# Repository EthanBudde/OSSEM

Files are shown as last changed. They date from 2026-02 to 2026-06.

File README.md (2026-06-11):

# OSSEM
OSSEM organization repo

Espresso brewing is a thermo-fluid process where temperature, pressure, flow rate, and time directly effect extraction and flavor. Commercial smart espresso machines offer advanced control, but are expensive, closed-source, and difficult to adapt for experimental research. Existing open-source modifications improve accessibility but do not fully support research-grade measurement or instrumentation. 

This project focuses on building an open-source smart emissions monitor based on the Gaggia Classic Pro, using platforms such as Gaggiuino and Gaggia Mate for embedded control and data logging. The system will allow precise control of brewing parameters, including temperature, pressure, flow profiling, and shot timing. 

Working with the Healthy Buildings Research Lab and the Coffee Telesensing Lab at Portland State University, the machine will be adapted to support PTR-MS and UV-VIS spectroscopy for measuring volatile organic compounds (VOCs) released during espresso extraction. The result will be a flexible, open source platform that supports repeatable espresso brewing and controlled emissions research.

<p align="center">
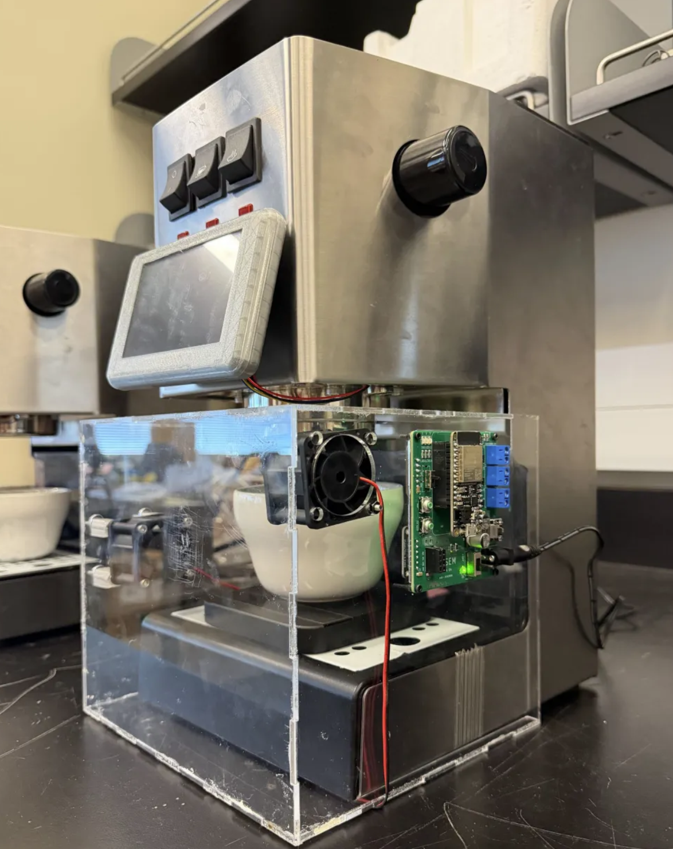
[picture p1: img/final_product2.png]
  
</p>

<p align="center">
  <em>Smart Emissions Monitor – Emissions Control Unit (ECU Final Product)</em>
</p>

<p align="center">
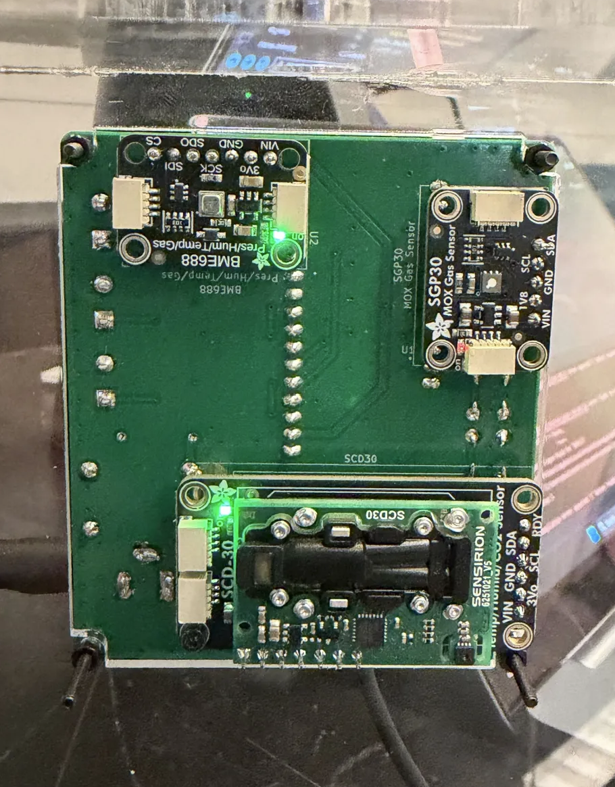
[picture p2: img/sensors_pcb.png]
  
</p>

<p align="center">
  <em>Emissions Control Unit Sensors</em>
</p>

<p align="center">
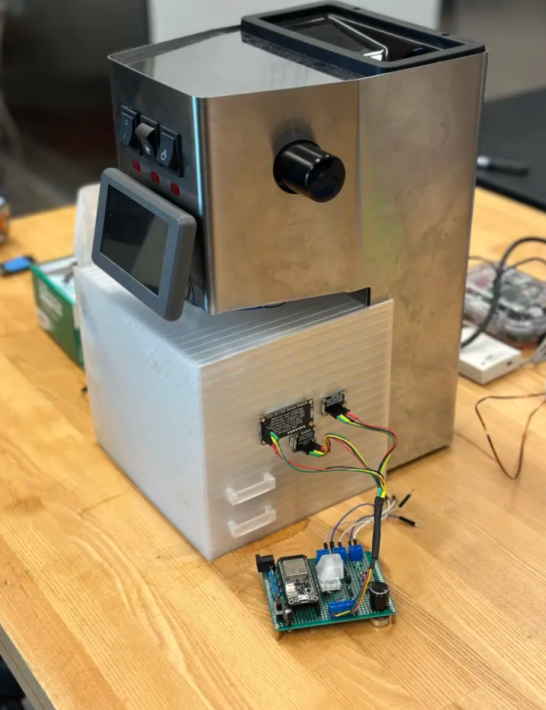
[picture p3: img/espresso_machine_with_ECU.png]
  
</p>

<p align="center">
  <em>Smart Emissions Monitor – Emissions Control Unit (ECU Prototype)</em>
</p>

<p align="center">
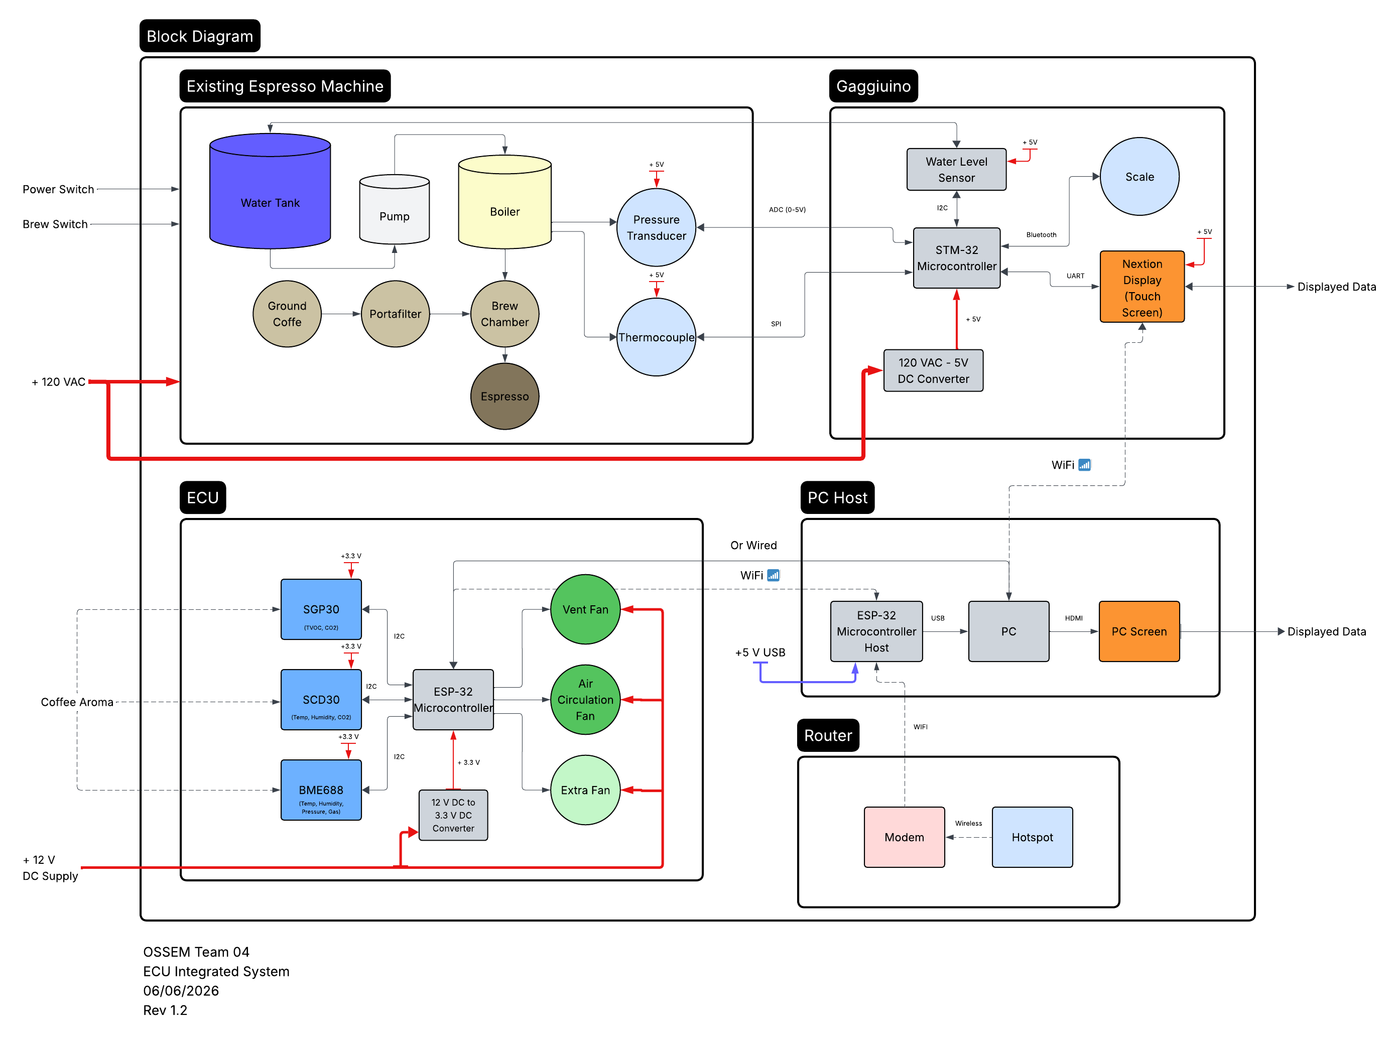
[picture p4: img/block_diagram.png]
  
</p>

<p align="center">
  <em>Smart Emissions Monitor – Block Diagram</em>
</p>

<p align="center">
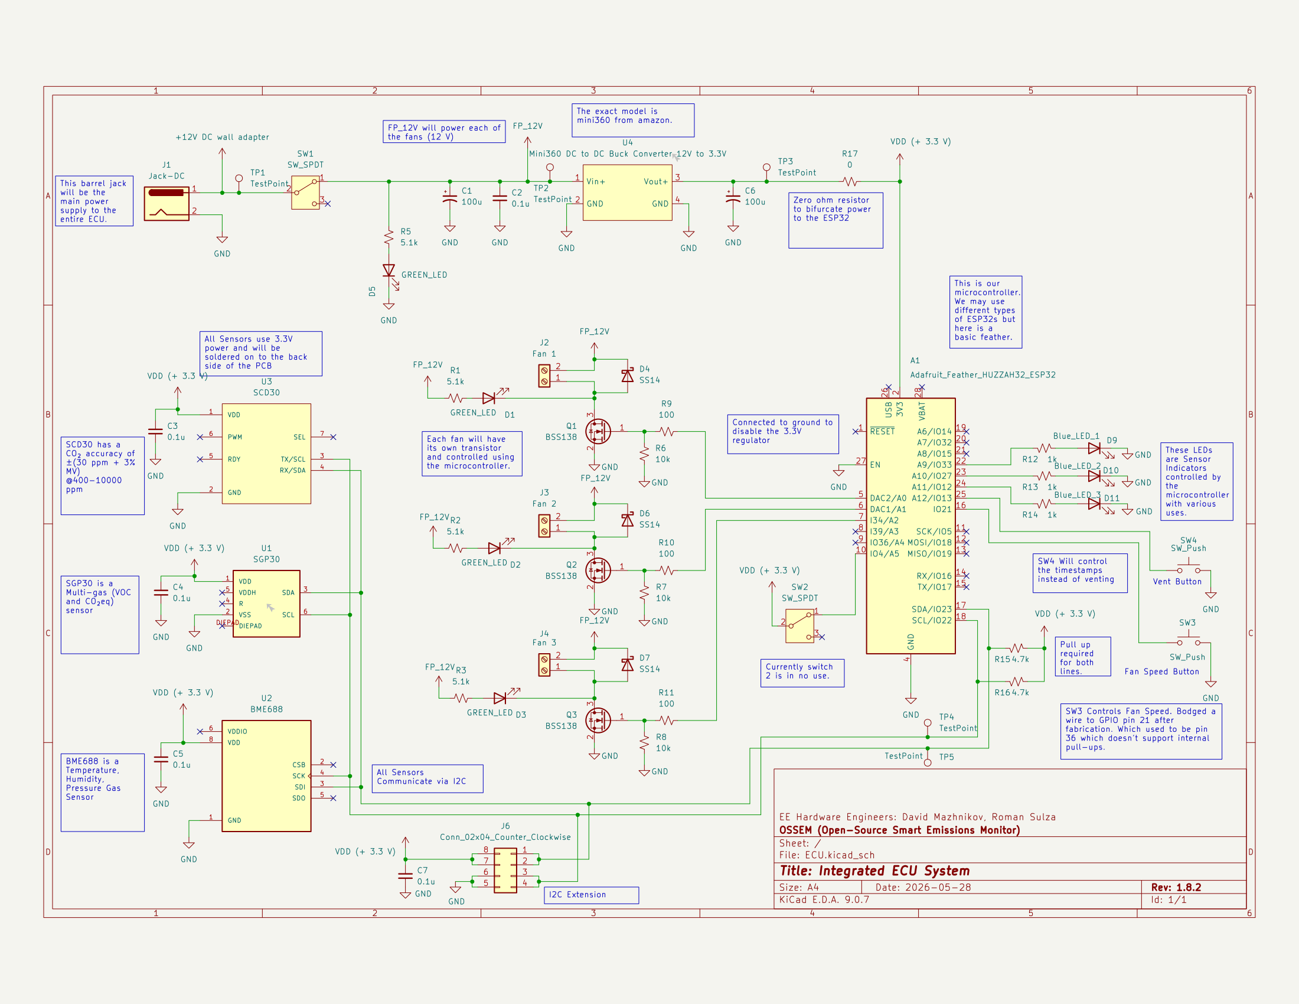
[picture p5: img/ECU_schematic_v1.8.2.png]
  
</p>

<p align="center">
  <em>Smart Emissions Monitor – Schematic v1.8.2</em>
</p>

<p align="center">
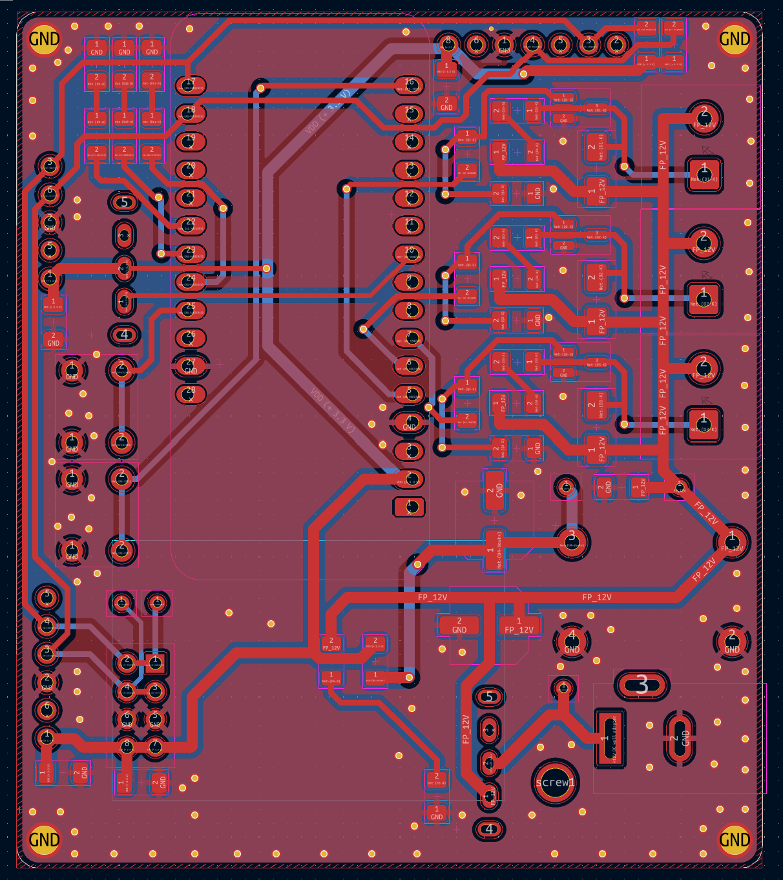
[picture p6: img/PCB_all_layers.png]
  
</p>

<p align="center">
  <em>Smart Emissions Monitor – PCB v1.8.2 </em>
</p>

<p align="center">
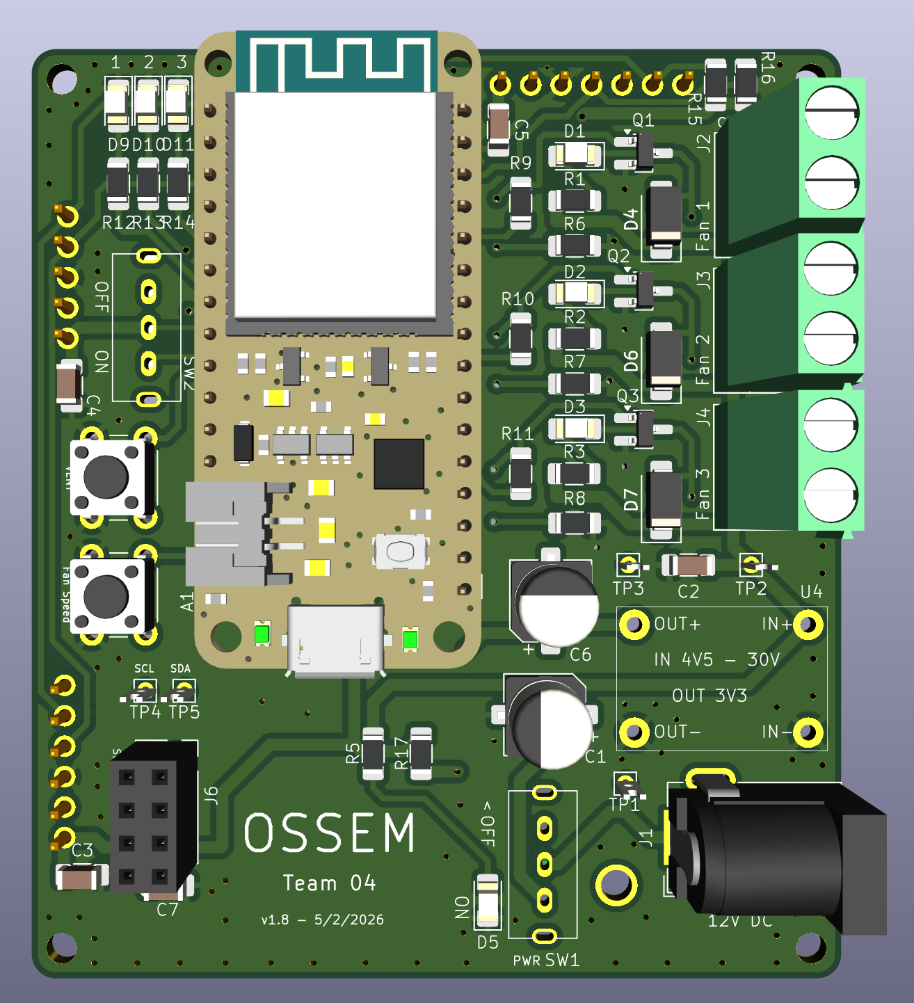
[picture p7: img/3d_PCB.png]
  
</p>

<p align="center">
  <em>Smart Emissions Monitor – 3D PCB v1.8 Front</em>
</p>

<p align="center">
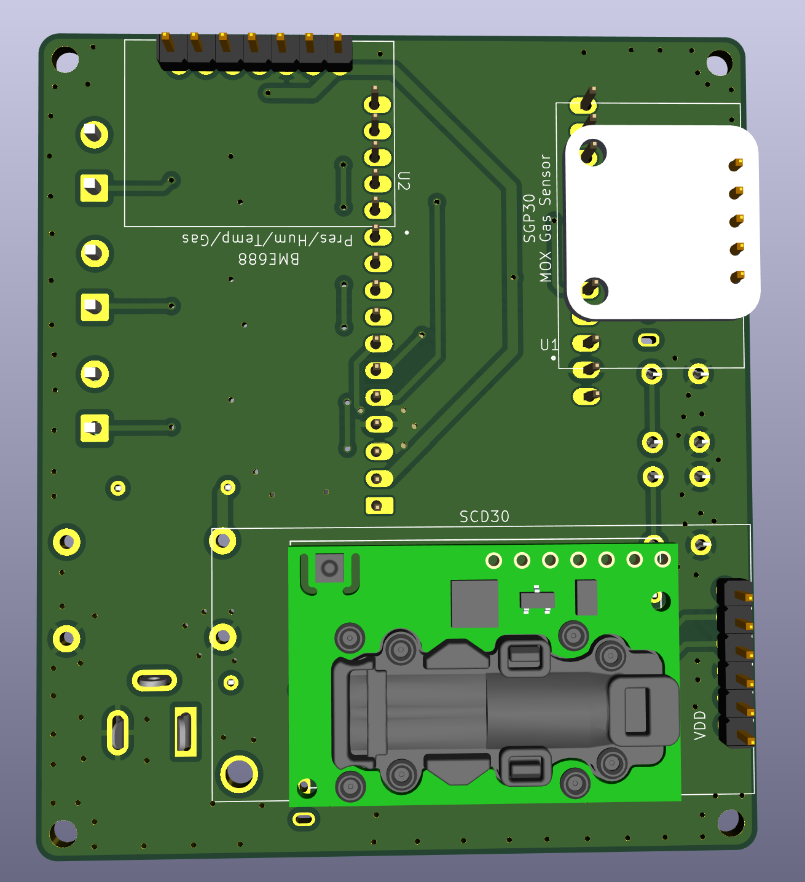
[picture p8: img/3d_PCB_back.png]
  
</p>

<p align="center">
  <em>Smart Emissions Monitor – 3D PCB v1.8 Back</em>
</p>

<p align="center">
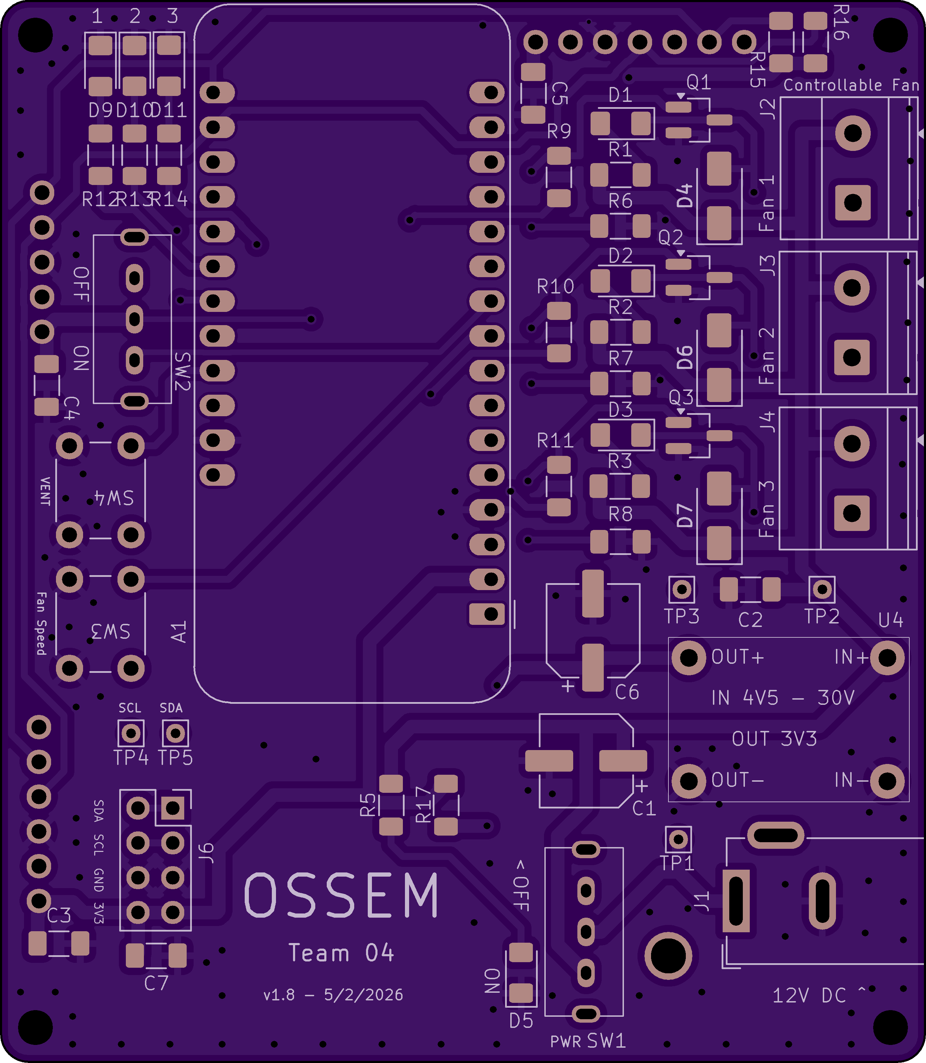
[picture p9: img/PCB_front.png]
  
</p>

<p align="center">
  <em>Smart Emissions Monitor – PCB v1.8 front</em>
</p>

<p align="center">
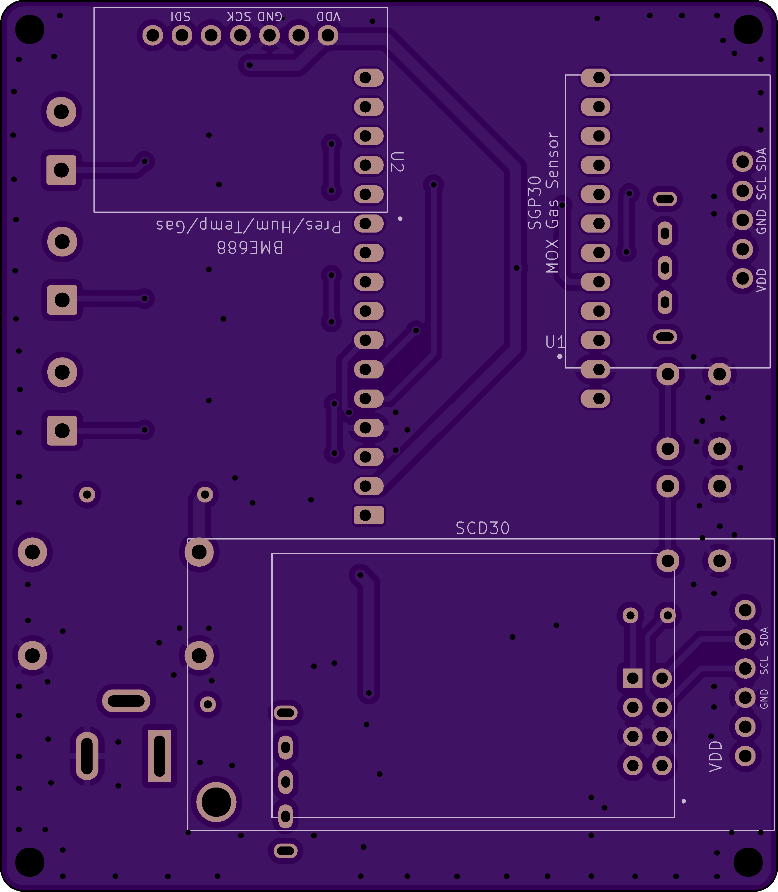
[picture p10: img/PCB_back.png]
  
</p>

<p align="center">
  <em>Smart Emissions Monitor – PCB v1.8 back</em>
</p>

<p align="center">
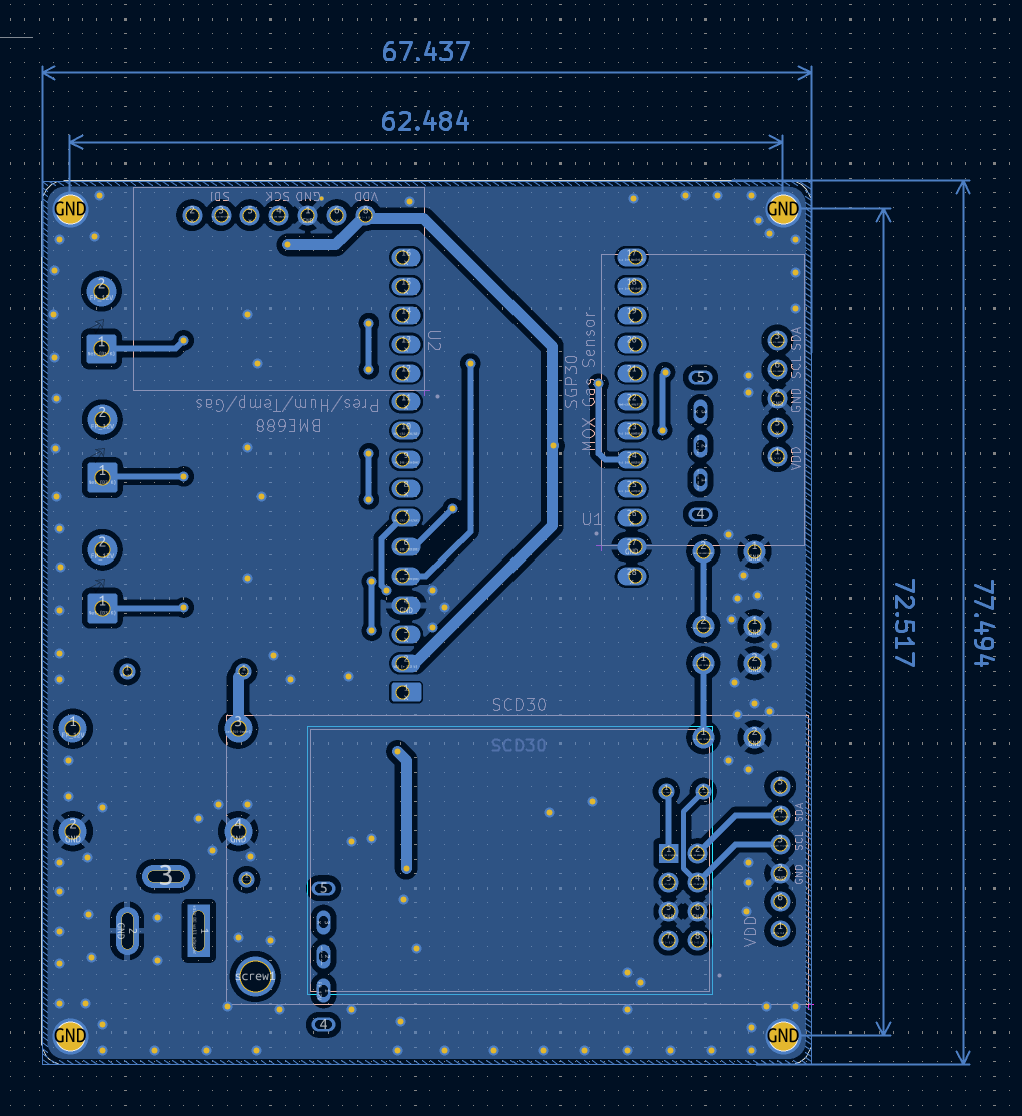
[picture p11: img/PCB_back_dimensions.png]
  
</p>

<p align="center">
  <em>Smart Emissions Monitor – PCB v1.8 back with dimensions</em>
</p>

## Acknowledgments
This project builds on:
- Gaggiuino (open-source espresso control system)
- Adafruit sensor libraries
- KiCad component libraries

PCB renders generated using OSH Park

All third-party resources are used in accordance with their respective licenses.

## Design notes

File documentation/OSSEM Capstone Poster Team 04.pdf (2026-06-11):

# Department of Electrical and Computer Engineering

# Open-source Smart Emissions Monitor

Team: Hussein Ashkanani, Ethan Budde, David Mazhnikov, Roman Sulza, Clarker Ren, Joseph Mazhnikov, John Abed, Phi Nguyen Faculty Advisors: Dr. Joshua Méndez & Dr. Elliott Gall ACKNOWLEDGEMENTS: Healthy Buildings Research Laboratory (HBRL) and Coffee and Telesensing Laboratory (COATL)

# OBJECTIVE

To develop an open-source smart emissions monitor for espresso brewing in collaboration with PSU’s Coffee and Telesensing Laboratory and Healthy Buildings Research Laboratory. The system combines a modified Gaggia Classic Pro, a custom PCB, environmental sensors, and an emissions enclosure to achieve consistent espresso brewing and repeatable emissions data collection.

# OVERVIEW

- Espresso brewing releases volatile organic compounds (VOCs) that affect indoor air quality
- Commercial smart machines are expensive, closed-source, and not designed for research
- Existing open-source modifications lack the sensing and instrumentation researchers need
- The Gaggiuino platform gives us a foundation for embedded control and data logging

# GAGGIUINO

- STM32 based functional enhancement for Gaggia Espresso Machines
- Temperature control for custom thermal, pressure, and flow profiling
- Bluetooth scale support with automatic brew stop by target weight
- Live brewing data via screen or Wi-Fi interface
- Includes local Wi-Fi connectivity for settings and monitoring

# METHODOLOGY

The team started with a Gaggiuino-modified Gaggia Classic Pro espresso machine, adding an emissions enclosure for VOC capture. An ESP32-based “Emissions Control Unit” PCB was designed for sensor reading and fan control within the enclosure.
The board integrates 3 sensors and 3 on-enclosure fans into a single PCB system. Sensor data is packetized and transmitted serially, with future design concepts utilizing network commands to a local webserver. Python tools were developed for data logging.

Figure 3: System block diagram

# TESTING & RESULTS

- Warm machine for a few minutes prior to brewing.
- Collect baseline data for 30 seconds.
- Pull a shot of espresso with the enclosure in place while simultaneously logging data using the sensor array.
- Collect post-brew data for 30 seconds.
- Remove enclosure and collect data for an additional 30 seconds.

Figure 1: Gaggia Espresso

Machine | Figure 2: Final design | COMPONENTS

Components used in the emissions monitor include sensors, a custom PCB and a ventilation system.

Figure 8: Custom PCB

Figure 9: Testing environment with PTR-MS | Figure 11: Espresso shot data, fan on slow speed
Figure 4: SCD30 sensor | Figure 5: BME688 sensor
Figure 6: SGP30 sensor | Figure 7: Mixing/External Fan

Figure 10: 3D Printed enclosure and PTR-MS

# CONCLUSION

- VOC and CO₂ emissions varied with roast age and brewing conditions.
- Methanol, Acetic Acid, Propionic Acid were among the primary compounds observed.
- Measurement speed and accuracy were limited by sensor design.
- Noisy environments create noisy data!

# FUTURE WORK

- Concurrent and post-shot regression analysis of data
- Integrating noise signals and environmental conditions
- Further system integration, including networking and onboard visualization.
- Successfully measured
temperature, humidity,
VOCs, CO₂ concentration,
and pressure throughout
brewing
- Observed correlation
between sensor data and
PTR-MS measurements
- Began parallel testing across multiple machines

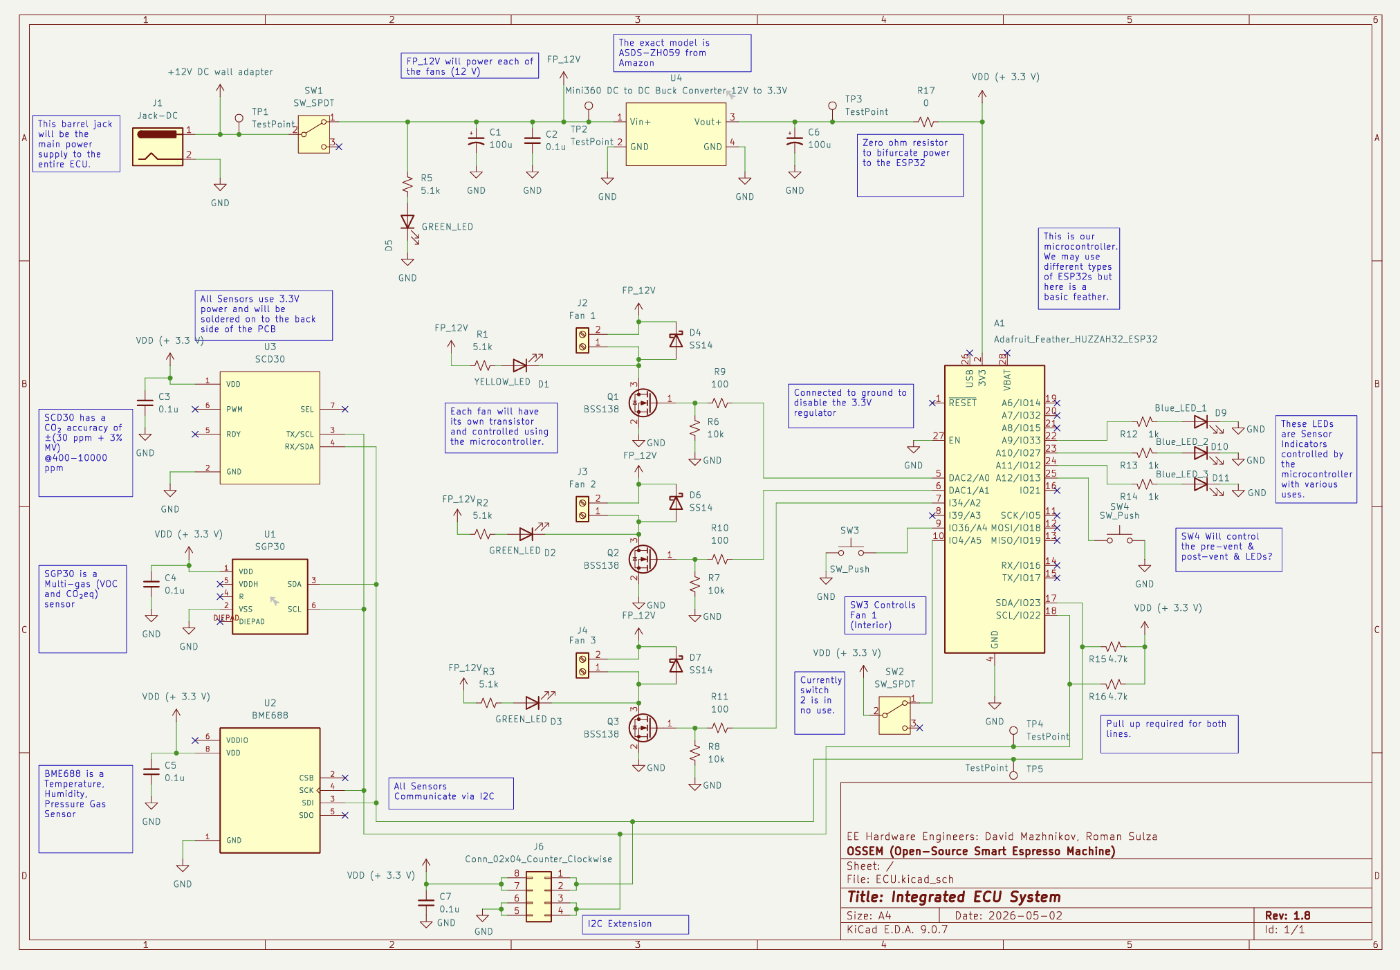
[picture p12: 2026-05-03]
img/ECU_schematic_v1.8.png

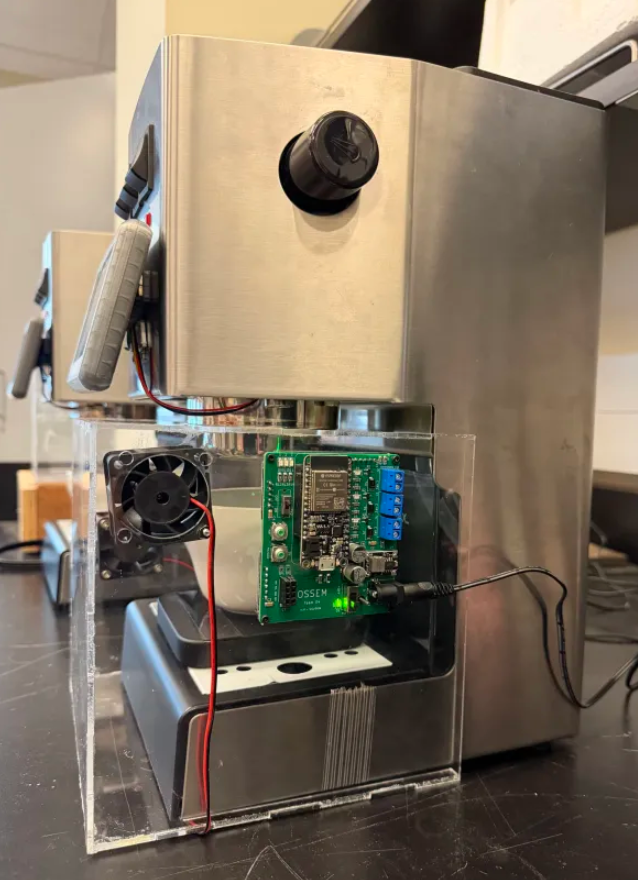
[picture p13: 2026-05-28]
img/final_product.png

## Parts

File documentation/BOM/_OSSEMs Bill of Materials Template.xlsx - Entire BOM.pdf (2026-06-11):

Bill Of Materials for: TEAM 4 - Open Source Smart Espresso Machine Last modified: 5/25/2026
BOM revision: 1.8
Qty | Mfr | Mfr Part Number Description | Dist | Dist Part Number Cost Ea. Cost Total Comments
4 Gaggia | RI9380/46 | Classic Pro E24 Espresso Machine 2024 | Amazon | B07RQ3NL76 | $457.08 $1,828.32 2 are donated? Are all these the same models? Are these bought from amazon?
2 GaggiMate | N/A | GaggiMate Pro Kit M4 K-Type + Pump Fittings | GaggiMate N/A | $212.00 | $424.00 Are these the right kits?
2 Gaggiuino | gen3-43-pro | Gaggiuino V4 PCB Kit 4.3″ Screen – GEN3 + Tank lvl + Scale | diy-efi | N/A | $325.00 | $650.00 Are these the right kits?
4 BaristaGadgets N/A | 12 Bar OPV Spring For Gaggia Classic PRO And EVO | Etsy | N/A | $12.00 | $48.00 Do we need all 4? Need to test each one if we need it or not
3 DigiKey | | ECU PCB total cost | | | $144.84 | $434.52 Price for 3 boards
1 Oshpark | | ECU PCB Fabbing costs | Oshpark | | $40.55 | $40.55 pack of 3
1 | | coffee beans | | | | $0.00
| | | | | TOTAL: | $3,425.39
VERSION INFO | | Comments

Rev
v1.8 | 5/11/2026
v1.8.1 | 5/25/2026

Links
https://www.amazon.com/Gaggia-RI9380-46-Espresso-Stainless/dp/B07RQ3NL76/ref=sr_1_1?crid=3OJE6MGPW61DH&dib=eyJ2IjoiMSJ9.eYjKLsAvj1W0J6UOi1cLWs7S2YO8OF4hQAQOlOF3g3hLJJjRMZuoTq9kSqRVxgfibjTNTAQokkwh8XOKxLYhOdfi3iOwWPR3rpvf6RqQUoixGFWXd-95crImEKKPH-aMxxHXEAhmxH4IVEVCKwkbWZhpCHDTMgAsxH_T5XagWTciojZHAUzSdV2V3VQgI8-yCoFLX5xq1GGfT73qabMzcHNR89k-2l4n2ZzoZgXIzuMGinX8iaTRX1HTunmR64dIo9db7rgI1Ui58Jy15TETksqra-XEj0mxnXHOiJN3FS8.pQ1m0DwROLVlKqMd-gxUtJx_k86bBO7aoHyDohzuF5U&dib_tag=se&keywords=Gaggia%2BClassic%2BPro%2BE24%2BEspresso%2BMachine&qid=1770954556&sprefix=gaggia%2Bclassic%2Bpro%2Be24%2Bespresso%2Bmachine%2Caps%2C223&sr=8-1&th=1 https://shop.gaggimate.eu/products/gaggimate-pro-kit
https://diy-efi.co.uk/product/gaggiuino-pro-kit-v4-gen3
https://www.etsy.com/listing/1556589768/12-bar-opv-spring-for-gaggia-classic-pro

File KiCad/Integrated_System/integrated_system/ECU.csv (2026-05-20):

Reference | Qty | Value | Description | Footprint | MANUFACTURER | MP | Datasheet
A1 | 1 | Adafruit_Feather_HUZZAH32_ESP32 | Microcontroller module with ESP32 MCU | Module:Adafruit_Feather | Adafruit |  | https://cdn-learn.adafruit.com/downloads/pdf/adafruit-huzzah32-esp32-feather.pdf
C1,C6 | 2 | 100u | Polarized capacitor, small US symbol | Capacitor_SMD:CP_Elec_6.3x7.7 | DigiKey |  | ~
C2,C3,C4,C5,C7 | 5 | 0.1u | Unpolarized capacitor, small symbol | Capacitor_SMD:C_1206_3216Metric_Pad1.33x1.80mm_HandSolder | DigiKey |  | ~
D1 | 1 | YELLOW_LED | Light emitting diode | LED_SMD:LED_1206_3216Metric_Pad1.42x1.75mm_HandSolder | DigiKey |  | ~
D2,D3,D5 | 3 | GREEN_LED | Light emitting diode | LED_SMD:LED_1206_3216Metric_Pad1.42x1.75mm_HandSolder | DigiKey |  | ~
D4,D6,D7 | 3 | SS14 | 40V 1A Schottky Diode, SMA | Diode_SMD:D_SMA | DigiKey |  | https://www.vishay.com/docs/88746/ss12.pdf
D9 | 1 | Blue_LED_1 | Light emitting diode | LED_SMD:LED_1206_3216Metric_Pad1.42x1.75mm_HandSolder | DigiKey |  | ~
D10 | 1 | Blue_LED_2 | Light emitting diode | LED_SMD:LED_1206_3216Metric_Pad1.42x1.75mm_HandSolder | DigiKey |  | ~
D11 | 1 | Blue_LED_3 | Light emitting diode | LED_SMD:LED_1206_3216Metric_Pad1.42x1.75mm_HandSolder | DigiKey |  | ~
J1 | 1 | Jack-DC | DC Barrel Jack | Connector_BarrelJack:BarrelJack_GCT_DCJ200-10-A_Horizontal | DigiKey |  | ~
J2 | 1 | Fan 1 | Generic screw terminal, single row, 01x02, script generated (kicad-library-utils/schlib/autogen/connector/) | TerminalBlock_Phoenix:TerminalBlock_Phoenix_MKDS-1,5-2-5.08_1x02_P5.08mm_Horizontal | DigiKey |  | ~
J3 | 1 | Fan 2 | Generic screw terminal, single row, 01x02, script generated (kicad-library-utils/schlib/autogen/connector/) | TerminalBlock_Phoenix:TerminalBlock_Phoenix_MKDS-1,5-2-5.08_1x02_P5.08mm_Horizontal | DigiKey |  | ~
J4 | 1 | Fan 3 | Generic screw terminal, single row, 01x02, script generated (kicad-library-utils/schlib/autogen/connector/) | TerminalBlock_Phoenix:TerminalBlock_Phoenix_MKDS-1,5-2-5.08_1x02_P5.08mm_Horizontal | DigiKey |  | ~
J6 | 1 | Conn_02x04_Counter_Clockwise | Generic connector, double row, 02x04, counter clockwise pin numbering scheme (similar to DIP package numbering), script generated (kicad-library-utils/schlib/autogen/connector/) | Connector_PinSocket_2.54mm:PinSocket_2x04_P2.54mm_Vertical | DigiKey |  | ~
Q1,Q2,Q3 | 3 | BSS138 | 50V Vds, 0.22A Id, N-Channel MOSFET, SOT-23 | Package_TO_SOT_SMD:SOT-23_Handsoldering | DigiKey |  | https://www.onsemi.com/pub/Collateral/BSS138-D.PDF
R1,R2,R3,R5 | 4 | 5.1k | Resistor, small US symbol | Resistor_SMD:R_1206_3216Metric_Pad1.30x1.75mm_HandSolder | DigiKey |  | ~
R6,R7,R8 | 3 | 10k | Resistor, small US symbol | Resistor_SMD:R_1206_3216Metric_Pad1.30x1.75mm_HandSolder | DigiKey |  | ~
R9,R10,R11 | 3 | 100 | Resistor, small US symbol | Resistor_SMD:R_1206_3216Metric_Pad1.30x1.75mm_HandSolder | DigiKey |  | ~
R12,R13,R14 | 3 | 1k | Resistor, small US symbol | Resistor_SMD:R_1206_3216Metric_Pad1.30x1.75mm_HandSolder | DigiKey |  | ~
R15,R16 | 2 | 4.7k | Resistor, small US symbol | Resistor_SMD:R_1206_3216Metric_Pad1.30x1.75mm_HandSolder | DigiKey |  | ~
R17 | 1 | 0 | Resistor, small US symbol | Resistor_SMD:R_1206_3216Metric_Pad1.30x1.75mm_HandSolder | DigiKey |  | ~
SW1,SW2 | 2 | SW_SPDT | Switch, single pole double throw | switch_DM:switch_dm | DigiKey |  | ~
SW3,SW4 | 2 | SW_Push | Push button switch, generic, two pins | Button_Switch_THT:SW_PUSH_6mm | DigiKey |  | ~
TP1,TP2,TP3,TP4,TP5 | 5 | TestPoint | test point | Connector_Pin:Pin_D0.7mm_L6.5mm_W1.8mm_FlatFork | DigiKey |  | ~
U3 | 1 | SCD30 |  | SCD30:MODULE_SCD30 | Sensirion
U4 | 1 | Mini360 DC to DC Buck Converter 12V to 3.3V |  | Library:Mini360 | Amazon
U2 | 1 | BME688 |  | BME680:PSON80P300X300X100-8N | Bosch Sensortec | BME680
U1 | 1 | SGP30 |  | SGP30:SGP30 | Adafruit | SGP30

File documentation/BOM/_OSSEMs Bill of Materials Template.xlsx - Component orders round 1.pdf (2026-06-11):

Bill Of Materials for: TEAM 4 - Open Source Smart Espresso Machine Last modified: 2/23/2026
BOM revision: 1.0r1
Qty | Mfr | Mfr Part Number | Description | Dist | Dist Part Number Cost Ea. | Cost Total | Comments | Links
4 Sensirion | SHT40 | Temp/Humidity sensor | Adafruit | 4885 | $5.95 | $23.80 | https://www.adafruit.com/product/4885?srsltid=AfmBOor-G3Y08UFehkjBrZJl_1ohO81TSDiFq6n9P5MXHyIh9_Jythr6
2 Sensirion | SGP30 | TVOC sensor | Adafruit | 3709 | $17.50 | $35.00
4 Sensirion | STC31-C-R3 | CO2 sensor | Mouser | 403-STC31-C-R3 | $31.28 | $125.12 | https://www.mouser.com/ProductDetail/Sensirion/STC31-C-R3?qs=wT7LY0lnAe37rCJTiHe%252BrQ%3D%3D&utm_id=9491304176&utm_source=google&utm_medium=cpc&utm_marketing_tactic=amercorp&gad_source=1&gad_campaignid=9491304176&gclid=CjwKCAiAkvDMBhBMEiwAnUA9BS0FUsJTmBF2uRvVsmqSKQCmll1pmuDwEYrxInVqTBzZ3w86c7Lz1RoCEFAQAvD_BwE
4 Adafruit | N/A | microSD card reader | Adafruit | 4682 | $3.50 | $14.00 | https://www.adafruit.com/product/4682#technical-details
4 Sandisk | SDSQXVF-032G-AN6MA microSD card, 32Gb | Sandisk | N/A | $10.49 | $41.96 generic, can be bought elsewhere https://www.sandisk.com/products/memory-cards/microsd-cards/sandisk-extreme-uhs-i-microsd-160-mbps?sku=SDSQXVF-032G-AN6MA
1 DBit | N300 | WiFi router | Amazon | N/A | $19.99 | $19.99 doesn't have to be this one | https://www.amazon.com/Setup-Wireless-Wi-Fi-Router-Internet/dp/B0CGLWPS5T?adgrpid=187821077233&dib=eyJ2IjoiMSJ9.Nok0yJVI5JQrHH3ioK6vwmW0p57kY3Ahcop6uhNaZ7WOI6yofJoF2ATOQLQjTjsSOijmAmuodI0VpVtHC_SbwuGt3u20JfSQzoflAOFXbyQxn6sf8AYssmg0YxAGGTweHEl_8lm6CAI2iayAbyJWdquZMO4tz14IFnjo8IlqH3MekMqna1u2GpkjJmcpFc9WNxv2L209gv8nyhZsmCUq-QifDoHT8OeXtRDy6qKME3s.auvnQRRe4h6CUfRDSmM4-avIqgUTDcTb4Njg7G5U5V0&dib_tag=se&hvadid=779676863753&hvdev=c&hvexpln=0&hvlocphy=9032925&hvnetw=g&hvocijid=8159785600867422257--&hvqmt=e&hvrand=8159785600867422257&hvtargid=kwd-347025567326&hydadcr=24140_13858981_2335143&keywords=inexpensive+wifi+router&mcid=f0f822e3139338c0bbd46435e94e2274&qid=1771874551&sr=8-4
| | | | | TOTAL: | $259.87

https://www.adafruit.com/product/4885?srsltid=AfmBOor-G3Y08UFehkjBrZJl_1ohO81TSDiFq6n9P5MXHyIh9_Jythr6

https://www.mouser.com/ProductDetail/Sensirion/STC31-C-R3?qs=wT7LY0lnAe37rCJTiHe%252BrQ%3D%3D&utm_id=9491304176&utm_source=google&utm_medium=cpc&utm_marketing_tactic=amercorp&gad_source=1&gad_campaignid=9491304176&gclid=CjwKCAiAkvDMBhBMEiwAnUA9BS0FUsJTmBF2uRvVsmqSKQCmll1pmuDwEYrxInVqTBzZ3w86c7Lz1RoCEFAQAvD_BwE

https://www.sandisk.com/products/memory-cards/microsd-cards/sandisk-extreme-uhs-i-microsd-160-mbps?sku=SDSQXVF-032G-AN6MAhttps://www.amazon.com/Setup-Wireless-Wi-Fi-Router-Internet/dp/B0CGLWPS5T?adgrpid=187821077233&dib=eyJ2IjoiMSJ9.Nok0yJVI5JQrHH3ioK6vwmW0p57kY3Ahcop6uhNaZ7WOI6yofJoF2ATOQLQjTjsSOijmAmuodI0VpVtHC_SbwuGt3u20JfSQzoflAOFXbyQxn6sf8AYssmg0YxAGGTweHEl_8lm6CAI2iayAbyJWdquZMO4tz14IFnjo8IlqH3MekMqna1u2GpkjJmcpFc9WNxv2L209gv8nyhZsmCUq-QifDoHT8OeXtRDy6qKME3s.auvnQRRe4h6CUfRDSmM4-avIqgUTDcTb4Njg7G5U5V0&dib_tag=se&hvadid=779676863753&hvdev=c&hvexpln=0&hvlocphy=9032925&hvnetw=g&hvocijid=8159785600867422257--&hvqmt=e&hvrand=8159785600867422257&hvtargid=kwd-347025567326&hydadcr=24140_13858981_2335143&keywords=inexpensive+wifi+router&mcid=f0f822e3139338c0bbd46435e94e2274&qid=1771874551&sr=8-4

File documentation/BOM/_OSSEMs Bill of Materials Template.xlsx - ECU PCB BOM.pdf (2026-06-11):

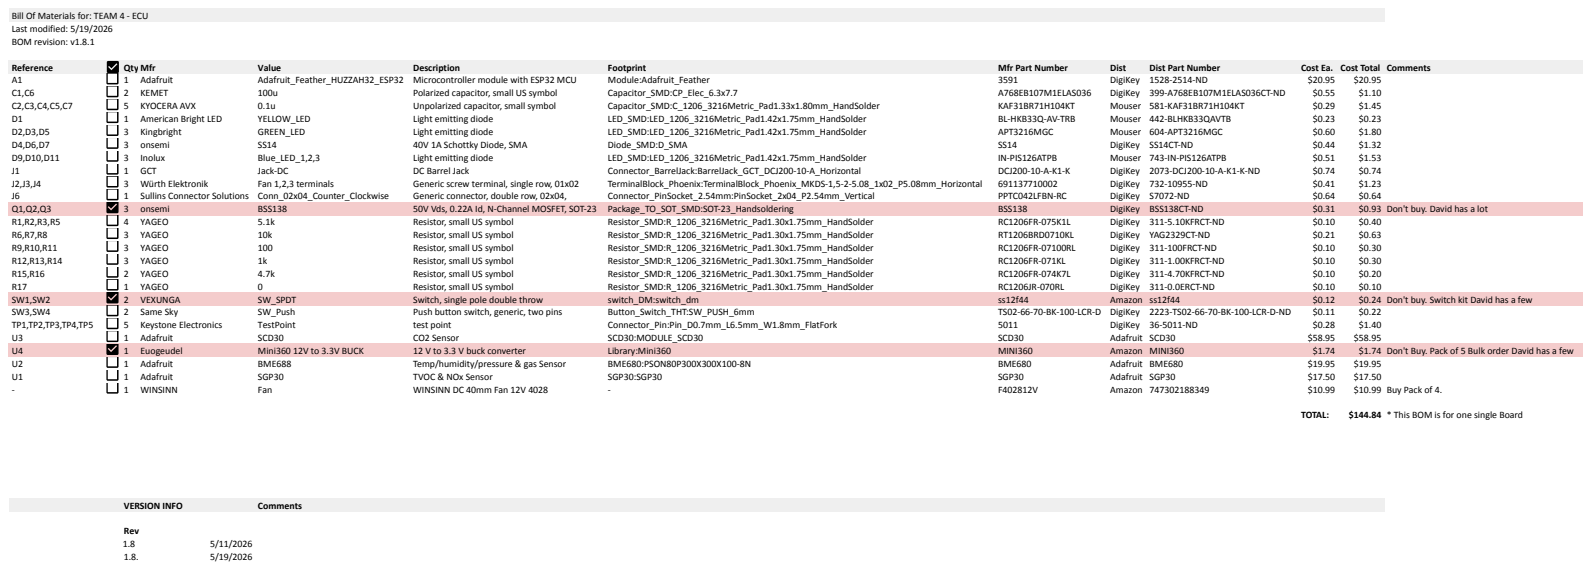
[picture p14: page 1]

Bill Of Materials for: TEAM 4 - ECU
Last modified: 5/19/2026 BOM revision: v1.8.1

Links https://www.digikey.com/en/products/detail/adafruit-industries-llc/3591/8119805?gclsrc=aw.ds&gad_source=1&gad_campaignid=20243136172&gbraid=0AAAAADrbLlhzLx615ba9QK59Pt4o19z2d&gclid=CjwKCAjwzevPBhBaEiwAplAxvjMS0UebVL3pfVtJB-cmnz0C0aDQNIIBjvmk42GUCftOvSaBqtOfDRoC3F0QAvD_BwE | https://cdn-learn.adafruit.com/downloads/pdf/adafruit-huzzah32-esp32-feather.pdf https://www.digikey.com/en/products/detail/kemet/A768EB107M1ELAS036/13420071?_gl=1*1azxihs*_up*MQ..*_gs*MQ.. https://www.mouser.com/ProductDetail/KYOCERA-AVX/KAF31BR71H104KT?qs=Jm2GQyTW%2Fbiqw6WjbGTB4g%3D%3D

https://www.mouser.com/ProductDetail/American-Bright-LED/BL-HKB33Q-AV-TRB?qs=Y0Uzf4wQF3l5aAeA8gsNCw%3D%3Dhttps://www.mouser.com/ProductDetail/Kingbright/APT3216MGC?qs=85uWm5%252BqJhXwVT90wiXd0g%3D%3D
https://www.digikey.com/en/products/detail/onsemi/SS14/965474 | https://www.vishay.com/docs/88746/ss12.pdf https://www.mouser.com/ProductDetail/Inolux/IN-PIS126ATPB?qs=G4MbTVxgV4GdC%252B%2F7gWg4nw%3D%3D
https://www.digikey.com/en/products/detail/gct/DCJ200-10-A-K1-K/9859579 https://www.digikey.com/en/products/detail/w%C3%BCrth-elektronik/691137710002/6644051 https://www.digikey.com/en/products/detail/sullins-connector-solutions/PPTC042LFBN-RC/810211 https://www.digikey.com/en/products/detail/onsemi/BSS138/244210 | https://www.onsemi.com/pub/Collateral/BSS138-D.PDF https://www.digikey.com/en/products/detail/yageo/RC1206FR-075K1L/728947 https://www.digikey.com/en/products/detail/yageo/RT1206BRD0710KL/1079472 https://www.digikey.com/en/products/detail/yageo/RC1206FR-07100RL/728491 https://www.digikey.com/en/products/detail/yageo/RC1206FR-071KL/728387 https://www.digikey.com/en/products/detail/yageo/RC1206FR-074K7L/728887 https://www.digikey.com/en/products/detail/yageo/RC1206JR-070RL/729184 https://www.amazon.com/dp/B0FG2TSLFC?ref=ppx_yo2ov_dt_b_fed_asin_title https://www.digikey.com/en/products/detail/same-sky-formerly-cui-devices-/TS02-66-70-BK-100-LCR-D/15634375?gclsrc=aw.ds&gad_source=1&gad_campaignid=20243136172&gbraid=0AAAAADrbLlhzLx615ba9QK59Pt4o19z2d&gclid=CjwKCAjwzevPBhBaEiwAplAxvv05tiw5cxMKHEIVxApXS9Wkp_bn8_xQFE9yDjJJWQSEgau41IJNmBoCpNAQAvD_BwE https://www.digikey.com/en/products/detail/keystone-electronics/5011/255333?gclsrc=aw.ds&gad_source=1&gad_campaignid=20228387720&gbraid=0AAAAADrbLlg9c50h6VvdakiVyJlQI8ZUM&gclid=CjwKCAjwzevPBhBaEiwAplAxvneNRsBU5R2wlxwfkJ7Gw7UYle7eGH3WnVuUGJn3NhPefgVtUH8TshoCnboQAvD_BwE https://www.adafruit.com/product/4867?srsltid=AfmBOopUPcTik5R2PO1EXHg9ZWgs2Y4jIcgymbVyIzx_xBf9B6JA89ov https://www.amazon.com/dp/B0BVFYXPQ8?ref=ppx_yo2ov_dt_b_fed_asin_title&th=1 https://www.adafruit.com/product/5046?gad_source=1&gad_campaignid=642608547&gbraid=0AAAAADx9JvSyw7y6eC_0nI95rRCuwBXqs&gclid=CjwKCAjwzevPBhBaEiwAplAxvum0O3m37Qx6Yu7pL77do2Y3pFkyOlGOD-MY3JrO3A6TvI0_rkeDdBoCuVoQAvD_BwE https://www.adafruit.com/product/3709?srsltid=AfmBOorbfc38_rf33Igl14sY4RIQvwuWvfZmwvBepgxOHmZKZLNTboNX https://www.amazon.com/dp/B0D3FXFG93?ref=ppx_yo2ov_dt_b_fed_asin_title

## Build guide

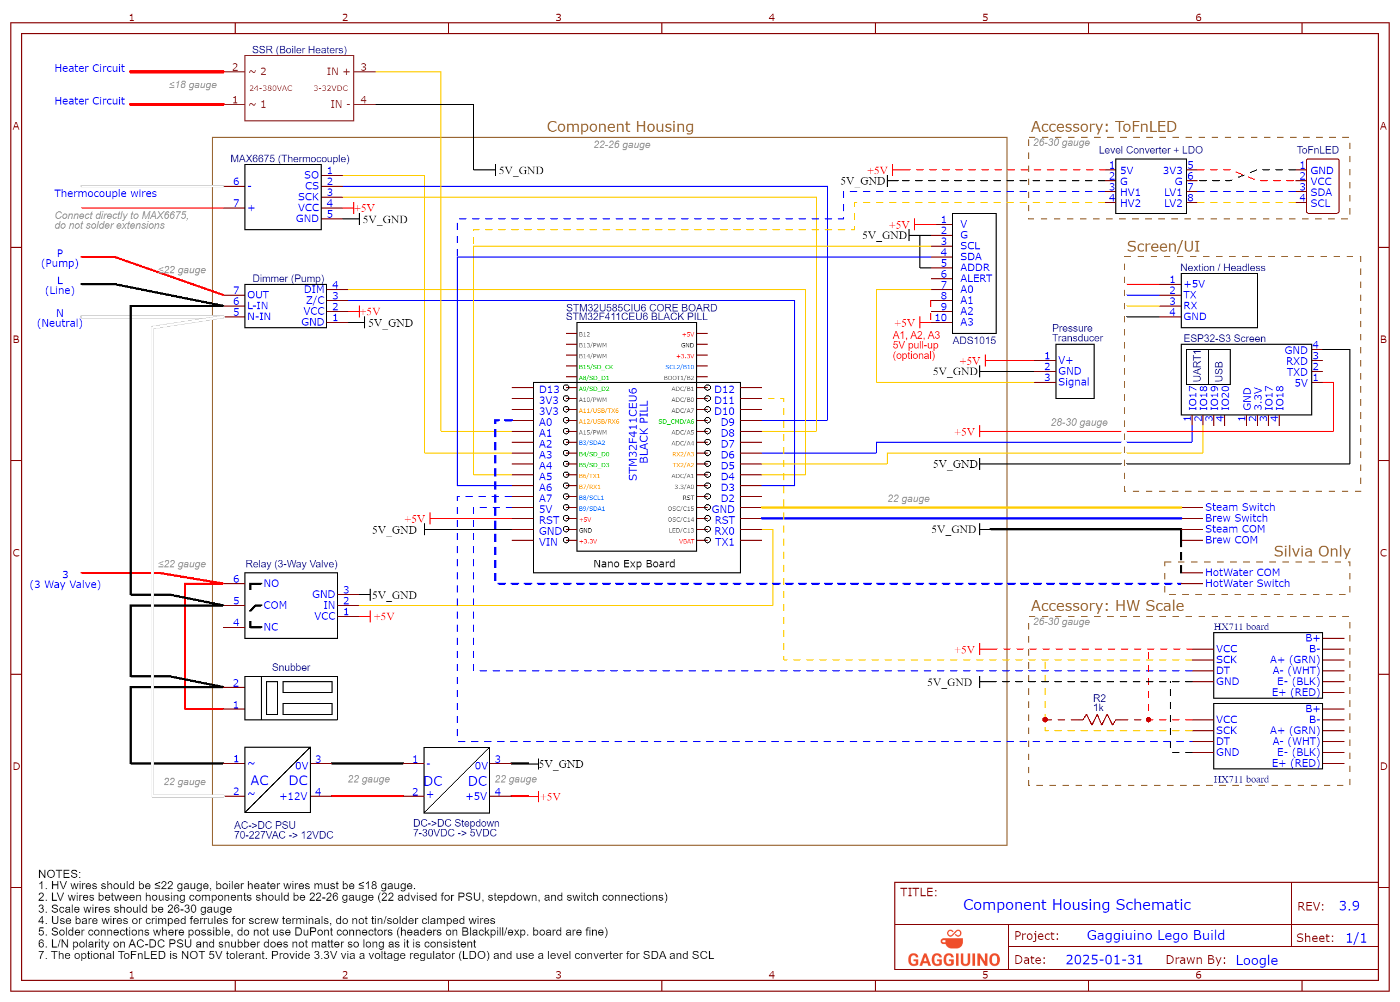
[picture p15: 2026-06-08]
img/stm32-comp-build.png

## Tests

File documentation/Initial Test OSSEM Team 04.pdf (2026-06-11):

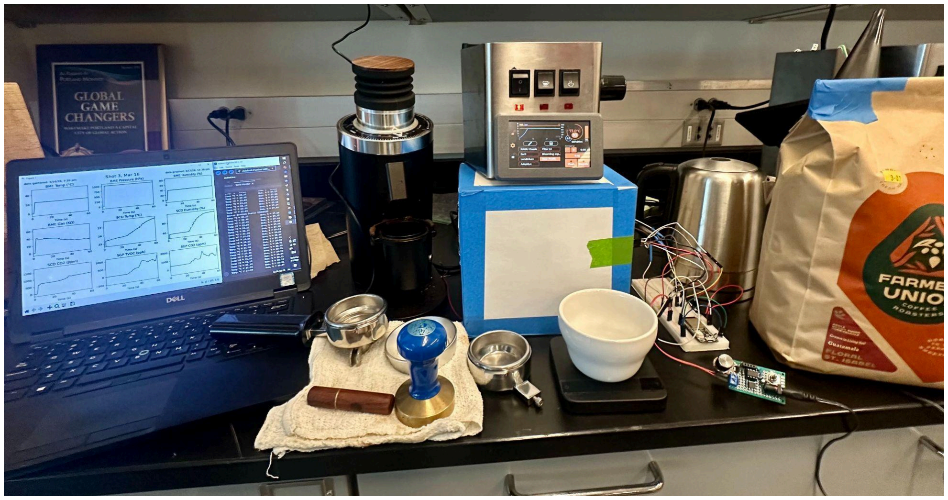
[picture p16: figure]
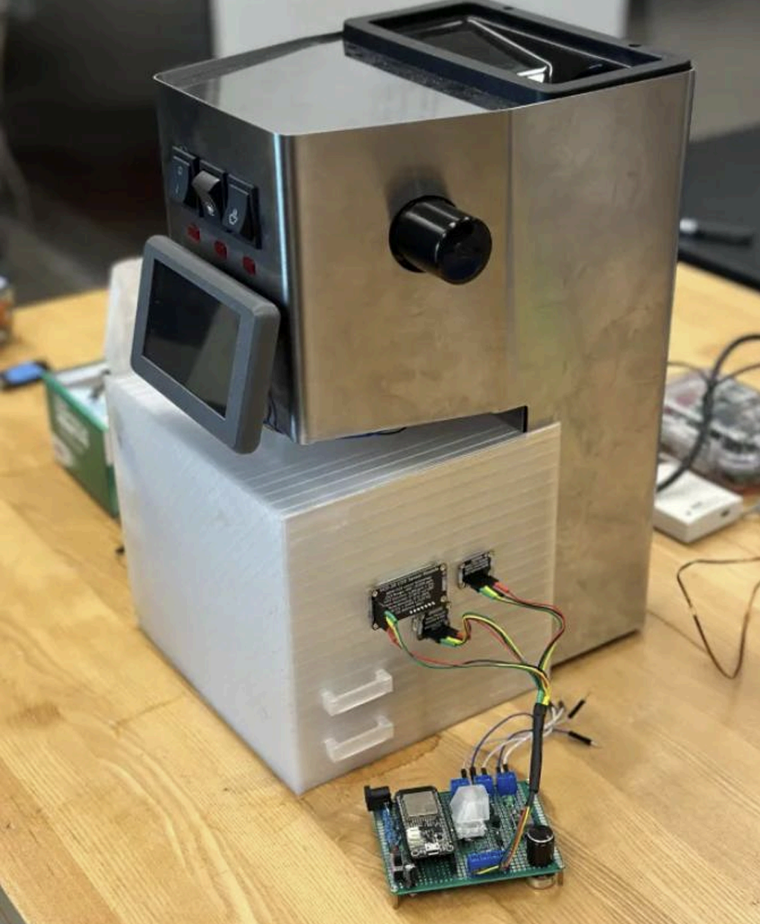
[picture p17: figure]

# OSSEM Initial Test

2026/04/30

Team Members: Hussein Ashkanani, Ethan Budde, David Mazhnikov, Roman Sulza, Clarker Ren

### Table of Contents

Table of Contents | 2
Top Down Test Plan v1.0 | 3
Purpose | 3
Equipment Needed | 3
Pre-Test Setup | 4
Top Down Test Steps | 4
Pre-Test Checks | 4
1.0 Espresso Machine / ECU power check | 4
1.1 Pre-Vent Check | 4
1.2 Espresso Machine Temperature Check | 4
1.3 Hardware Pre-Check | 4
1.4 Brew Enable Check | 5
1.5 Data Logging Check | 5
1.6 Network Communications Check | 5
1.7 Circulation Fan Check | 5
1.8 Scale Enable Check | 5
1.9 Visual Test | 5
Post-Test Checks | 6
2.0 Fan Post-Vent Check | 6
2.1 Data Validity Check | 6
2.2 Shot Weight Confirm | 6
2.3 Shot Quality Check | 6
2.4 Hardware Post-Check | 6
Post-Test Teardown | 6
Conclusions / Discussion | 7

### Top Down Test Plan v1.0

Date of Test: | 2026/04/30
Testers: | Ethan B. Computer / Embedded System Engineer David M. Integration / Hardware Engineer Roman S. Hardware Engineer …

Purpose
To test the full espresso emissions system and verify that the espresso machine, emissions chamber, airflow system, sensors, scale, data logging, and wireless communications function correctly before, during, and after a brew cycle.

Equipment Needed
- System Equipment
- Gaggia Espresso Machine (Gaggiuino Installed)
- Emissions Control Unit (ECU) / Emissions chamber
- 3 Fans
■ 2 fans for intake and exhaust ventilation
■ 1 fan for internal air circulation
- ESP32 Controllers
- Scale
- SGP30, SCD30 and BME680 Sensors
- Power supply to espresso machines (120V) and ECU (3.3V & 12V)
- Water and coffee beans
- Coffee Grinder
- Portafilter and Cup
- Coffee Tamper
- Espresso Coffee Stirrer (WDT)
- Test Equipment
- Laptop or computer for live data display
- USB cable to power ESP32 for setup/programming
- Network connection / Hotspot / Wi-Fi access
- Other Equipment
- Paper Towels / Cleanup materials / Sink
- Notebook or spreadsheet for logging
- Safety gloves if needed for hot surfaces (such as portafilter)

Pre-Test Setup
1. Place the espresso machine and ECU in the testing environment.
2. Verify all power connections are secure.
3. Verify the ESP32 boards are powered and programmed.
4. Connect the scale, sensors, fans, and communication modules.
5. Connect the computer to the monitoring interface.
6. Fill the espresso machine water reservoir and prepare the machine for brewing.
7. Weigh 18 grams of coffee beans and grind them in the coffee grinder (using the appropriate grind size).
8. Load the portafilter with the ground coffee and use the espresso coffee stirrer to stir the ground coffee, and use the tamper to tamp the ground coffee.
9. Confirm that the chamber is properly assembled and that the airflow path is not obstructed.

Top Down Test Steps

Pre-Test Checks

### 1.0 Espresso Machine / ECU power check

Objective: Verify the espresso machine and ECU power on correctly.
Procedure: Turn on system power.
Expected result: All devices power on without errors. Indicator LEDs, and display are working.
Pass/Fail: | Pass | .
Comments: ____________

### 1.1 Pre-Vent Check

Objective: Verify the 3 fans operate correctly before testing. Procedure:
- With a press of a button all 3 fans turn on for 30 seconds.
- Observe airflow direction and operation
Expected Result:
- Intake and exhaust fans move air through the chamber as intended.
- Internal fan circulates air inside the chamber
- No unusual vibration, noise, or fan stoppage occurs.
Pass/Fail: | Partial | .
Comments: Currently, only one internal fan works for now.

### 1.2 Espresso Machine Temperature Check

Objective: Confirm the machine is at brew-ready temperature (93 Degrees Celsius) Procedure: Check machine temperature from the Gaggiuino display.
Expected Result: Temperature is within acceptable brew range defined by the team. Measured Value: _____93.2 Celsius_______
Pass/Fail: | Pass | .
Comments: Slightly higher than expected.

### 1.3 Hardware Pre-Check

Objective: Confirm all hardware is connected.
Procedure: Inspect wiring, mounts, chamber seals, fan mounts, sensors, and scale placement. Expected Result: No loose wiring, missing parts, disconnected hardware, or damage.
Pass/Fail: | Partial | .
Comments: Two of 3 fans were not connected because we need to 3d model fan cutout on the enclosure.

### 1.4 Brew Enable Check

Objective: Verify the system allows brewing.
Procedure: Start a brew cycle.
Expected Result: The brew cycle begins successfully and the system operates normally.
Pass/Fail: | Pass | .
Comments: _____N/A_____

### 1.5 Data Logging Check

Objective: Verify system data is recorded during the shot.
Procedure: Pull a shot and observe whether sensor readings, timestamps, and other test data are logged. Expected Result: Data is continuously recorded during the brew without interruption.
Pass/Fail: | Pass | .
Comments: _____N/A_____

### 1.6 Network Communications Check

Objective: Verify wireless communication between ESP32 devices and the computer display. Procedure:
- Start system comms
- Confirm data from the ECU ESP32 is transmitted to the second ESP32 and PC.
- Observe the live data display
Expected Result:
- Wireless communication established
- Data updates appear correctly on the computer screen.
- No major dropouts or comms failures occur during the test
Pass/Fail: | Fail | .
Comments: Not yet working, will get it working soon…

### 1.7 Circulation Fan Check

Objective: Verify airflow control during the active shot.
Procedure: Observe fan operation while the shot is running.
Expected Result: Fans remain on and maintain expected airflow during the test.
Pass/Fail: | Partial | .
Comments: Kinda works but fans are too fast which gives unexpected data and not controlled by the main ECU hub as of right now.

### 1.8 Scale Enable Check

Objective: Verify the scale connects to Gaggiuino via Bluetooth and provides valid shot weight data. Procedure: Observe the scale before and during the shot.
Expected Result: The scale responds correctly, tracks weight change, and outputs readable data.
Pass/Fail: | Pass | .
Comments: _____N/A_____

### 1.9 Visual Test

Objective: Confirm correct overall system operation during the shot.
Procedure: Observe the machine, chamber, fan behavior, sensor, and live display during brewing. Expected Result:
- Brew occurs normally
- No leaks, disconnections, or unsafe behavior are observed (Although small amounts of splashing may be normal).
- The chamber remains intact
- Displayed data appears reasonable

Pass/Fail: | Pass | .
Comments: _____N/A_____

Post-Test Checks

### 2.0 Fan Post-Vent Check

Objective: Verify post-test ventilation clears the chamber after the shot.
Procedure: Leave the intake and exhaust fans running for the required post-shot vent period (30 seconds).
Expected Results: The chamber continues ventilating after shot completion for the planned duration.
Pass/Fail: | Pass | .
Comments: Need to manually turn on and off fan…

### 2.1 Data Validity Check

Objective: Confirm recorded data is reasonable and usable.
Procedure: Review collected logs after the test.
Expected Result: The data file is complete, timestamps are in order, and values are within expected ranges.
Pass/Fail: | Pass | .
Comments: BME680 gas resistance showing inverted data…

### 2.2 Shot Weight Confirm

Objective: Confirm measured shot weight is 36 grams.
Procedure: Compare the scale reading to the expected shot weight of 36 grams. Expected Result: Final shot weight is within 5% tolerance.
Measured Value: 35 -38 grams
Pass/Fail: | Pass | .
Comments: Shot is within 3-5 % tolerance

### 2.3 Shot Quality Check

Objective: Confirm the espresso shot is acceptable.
Procedure: Inspect crema, flow, shot appearance, and taste.
Expected Result: The shot completes with visual quality and taste quality.
Pass/Fail: | Pass | .
Comments: Tastes fruity, kinda of sweet, tangy etc..

### 2.4 Hardware Post-Check

Objective: Confirm hardware remains functional after the test.
Procedure: Inspect the system after the brew and vent cycle.
Expected Result: No overheated parts, disconnected wires, leaks, broken mounts, or other hardware issues.
Pass/Fail: | Pass | .
Comments: _____N/A_____

Post-Test Teardown
1. Stop brew operation
2. Shut down fans after the post-vent period is complete.
3. Save all recorded data files.
4. Power off electronics and the espresso machine.

5. Disconnect test equipment.
6. Clean the chamber, scale, empty the porta filter and wash in the sink or with a paper towel, and wipe the sensors with a paper towel if splash was present.
7. Record any failures, unexpected behavior, or follow-up actions.

Conclusions / Discussion
Overall Results: | Partial | .

Summary Notes:

The system was successful at a brew cycle with working data logging, sensors, and scale

integration. However, wireless communication is not yet functional, and fan installation/control is

incomplete, affecting airflow and data accuracy.

Requirements Verified:

Temperature, pressure, flow rate, data, shot profiling control, wireless scale, sensor integration,

and fan operation were partially verified. The chambered enclosure with sensors and ECU was also

tested.

Requirements Not Met / Issues Found:

Network comms and wireless comms between devices are not working yet. Only ⅓ of the fans are

currently installed and operating. Full ECU fan control still needs to be completed.

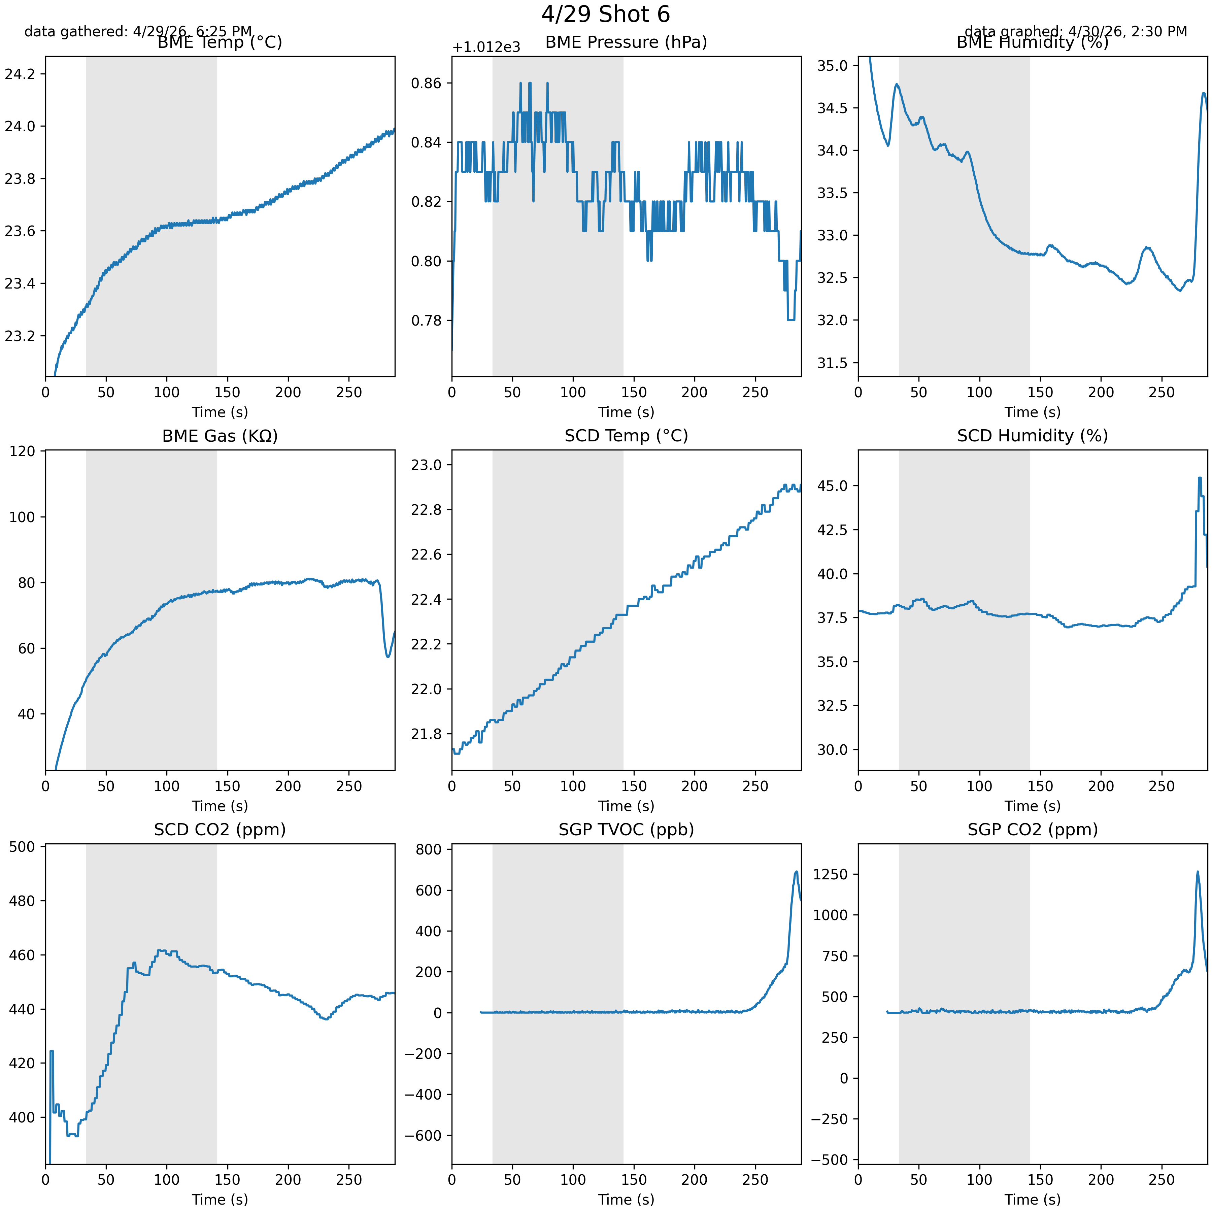
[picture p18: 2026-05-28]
py/test.png

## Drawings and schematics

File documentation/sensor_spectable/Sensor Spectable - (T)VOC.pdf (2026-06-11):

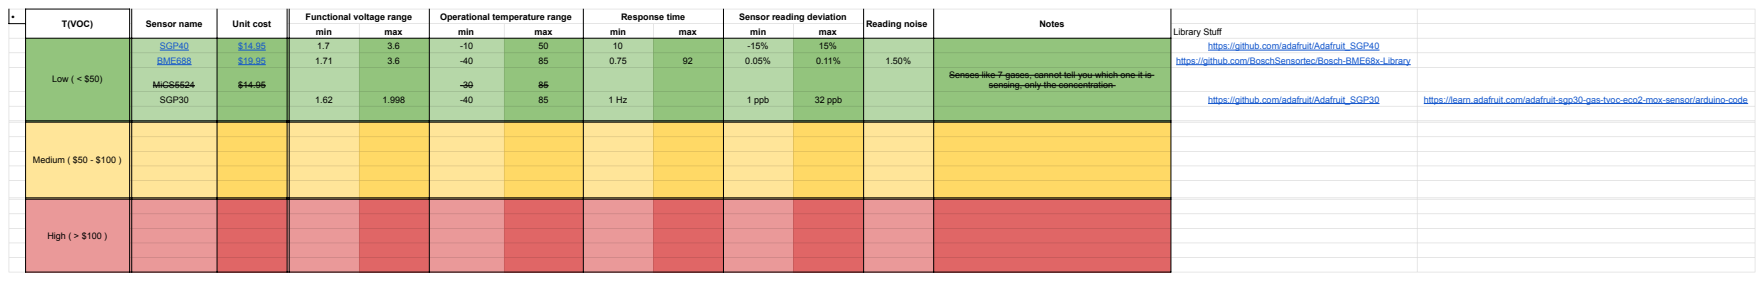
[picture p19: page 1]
T(VOC); Sensor name; Unit cost; Functional voltage range; Operational temperature range; Response time; Sensor reading deviation; Reading noise; Notes min; max; min; Library Stuff; Low ( < $50); SGP40; https://github.com/adafruit/Adafruit_SGP40 BME688; https://github.com/BoschSensortec/Bosch-BME68x-Library; MiCS5524; Senses like 7 gases, cannot tell you which one it is sensing, only the concentration SGP30; 1 ppb; 32 ppb; https://github.com/adafruit/Adafruit_SGP30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

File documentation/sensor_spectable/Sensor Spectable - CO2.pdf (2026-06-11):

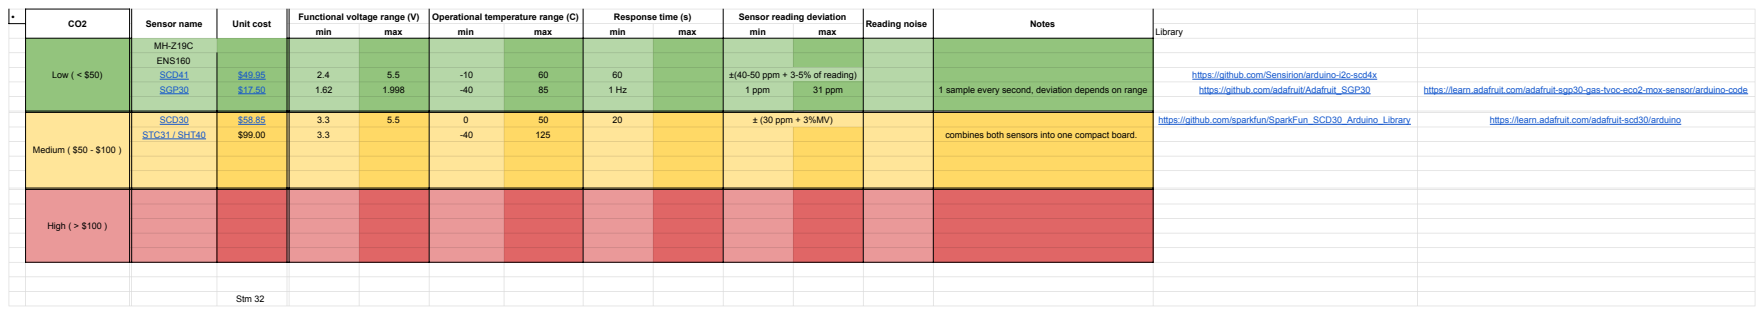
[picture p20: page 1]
Sensor name; Unit cost; Functional voltage range (V); Operational temperature range (C); Response time (s); Sensor reading deviation; Reading noise; Notes min; max; min; Library; Low ( < $50); ENS160 SCD41; ±(40-50 ppm + 3-5% of reading); https://github.com/Sensirion/arduino-i2c-scd4x SGP30; 1 ppm; 31 ppm; 1 sample every second, deviation depends on range; https://github.com/adafruit/Adafruit_SGP30; https://learn.adafruit.com/adafruit-sgp30-gas-tvoc-eco2-mox-sensor/arduino-code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

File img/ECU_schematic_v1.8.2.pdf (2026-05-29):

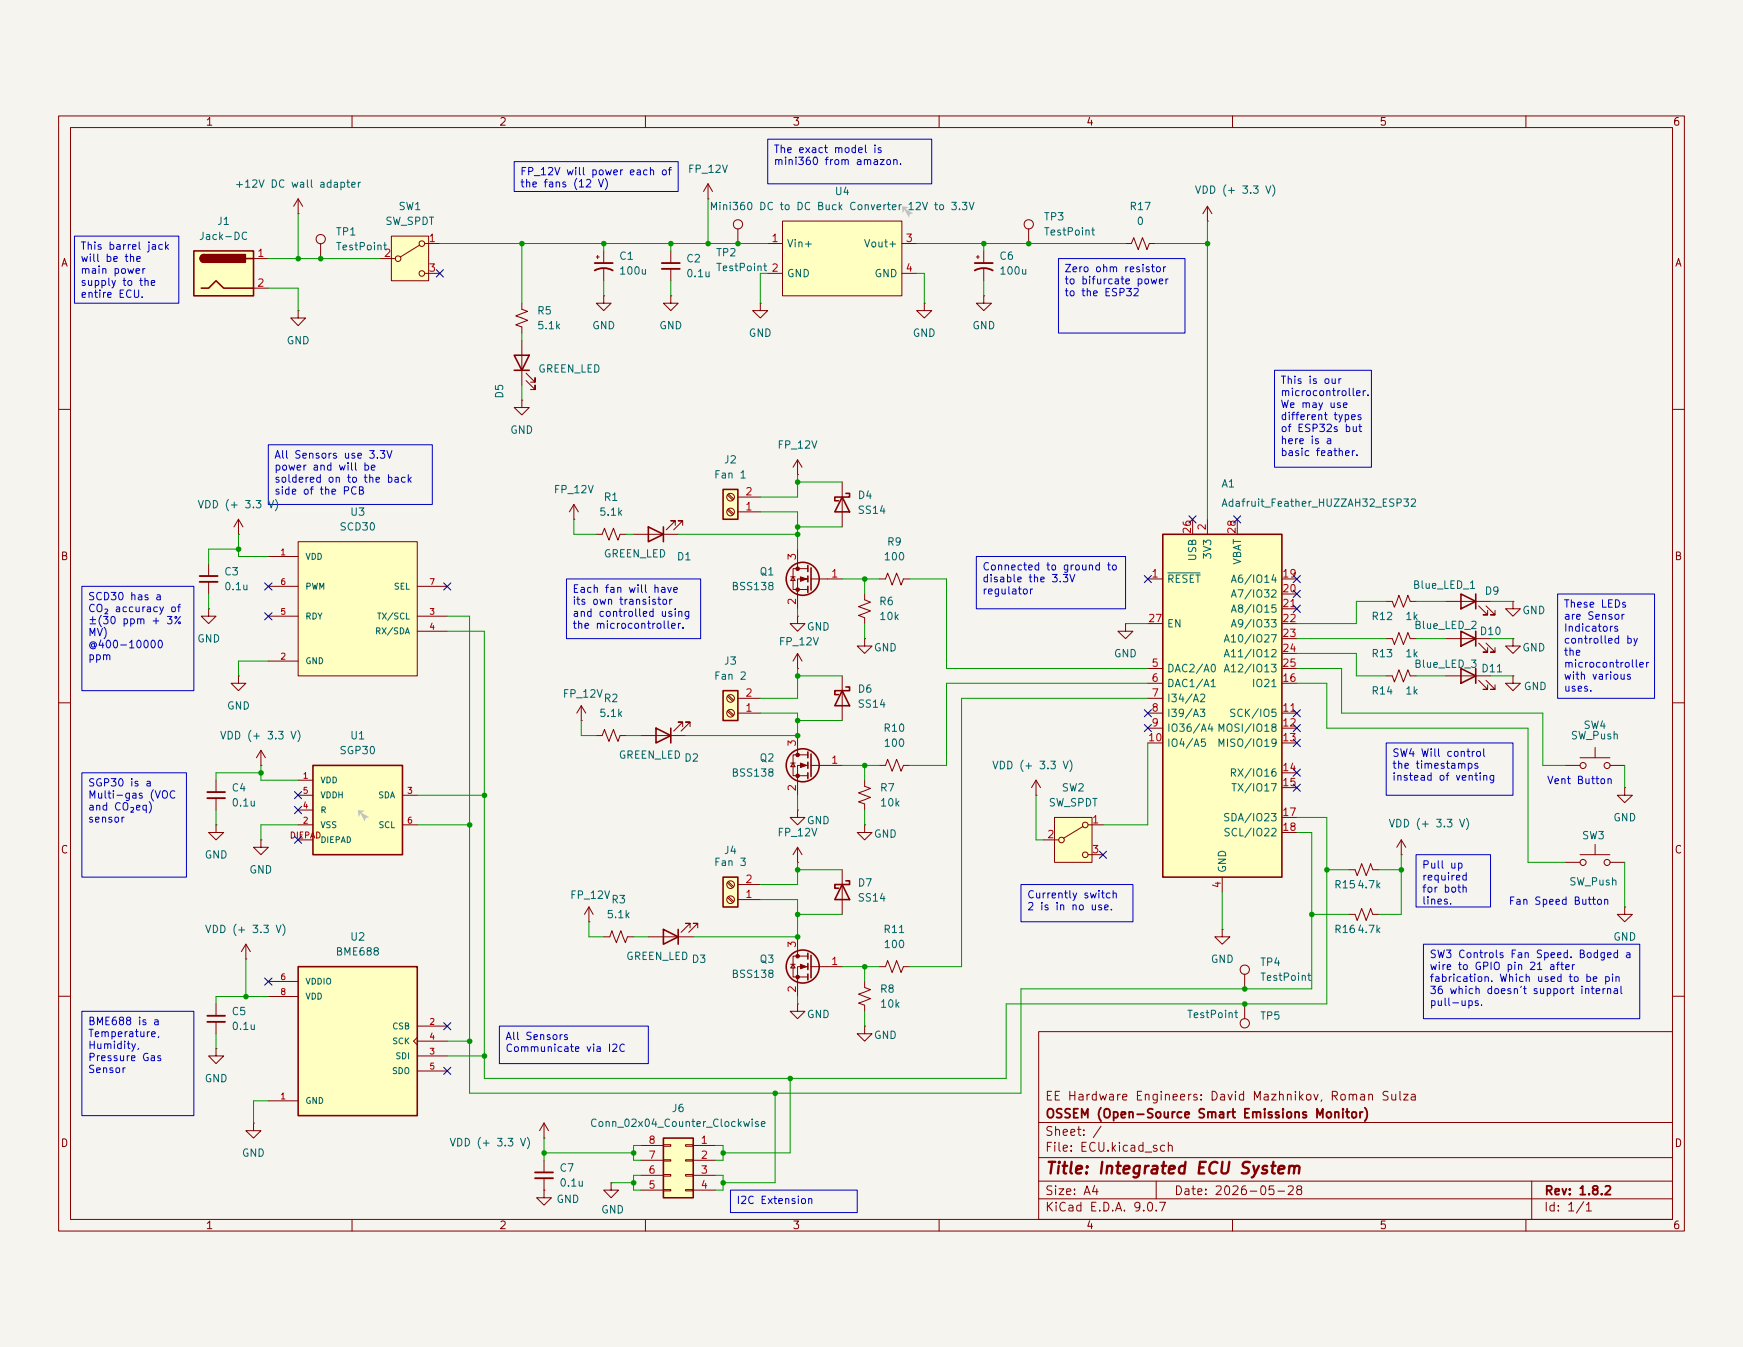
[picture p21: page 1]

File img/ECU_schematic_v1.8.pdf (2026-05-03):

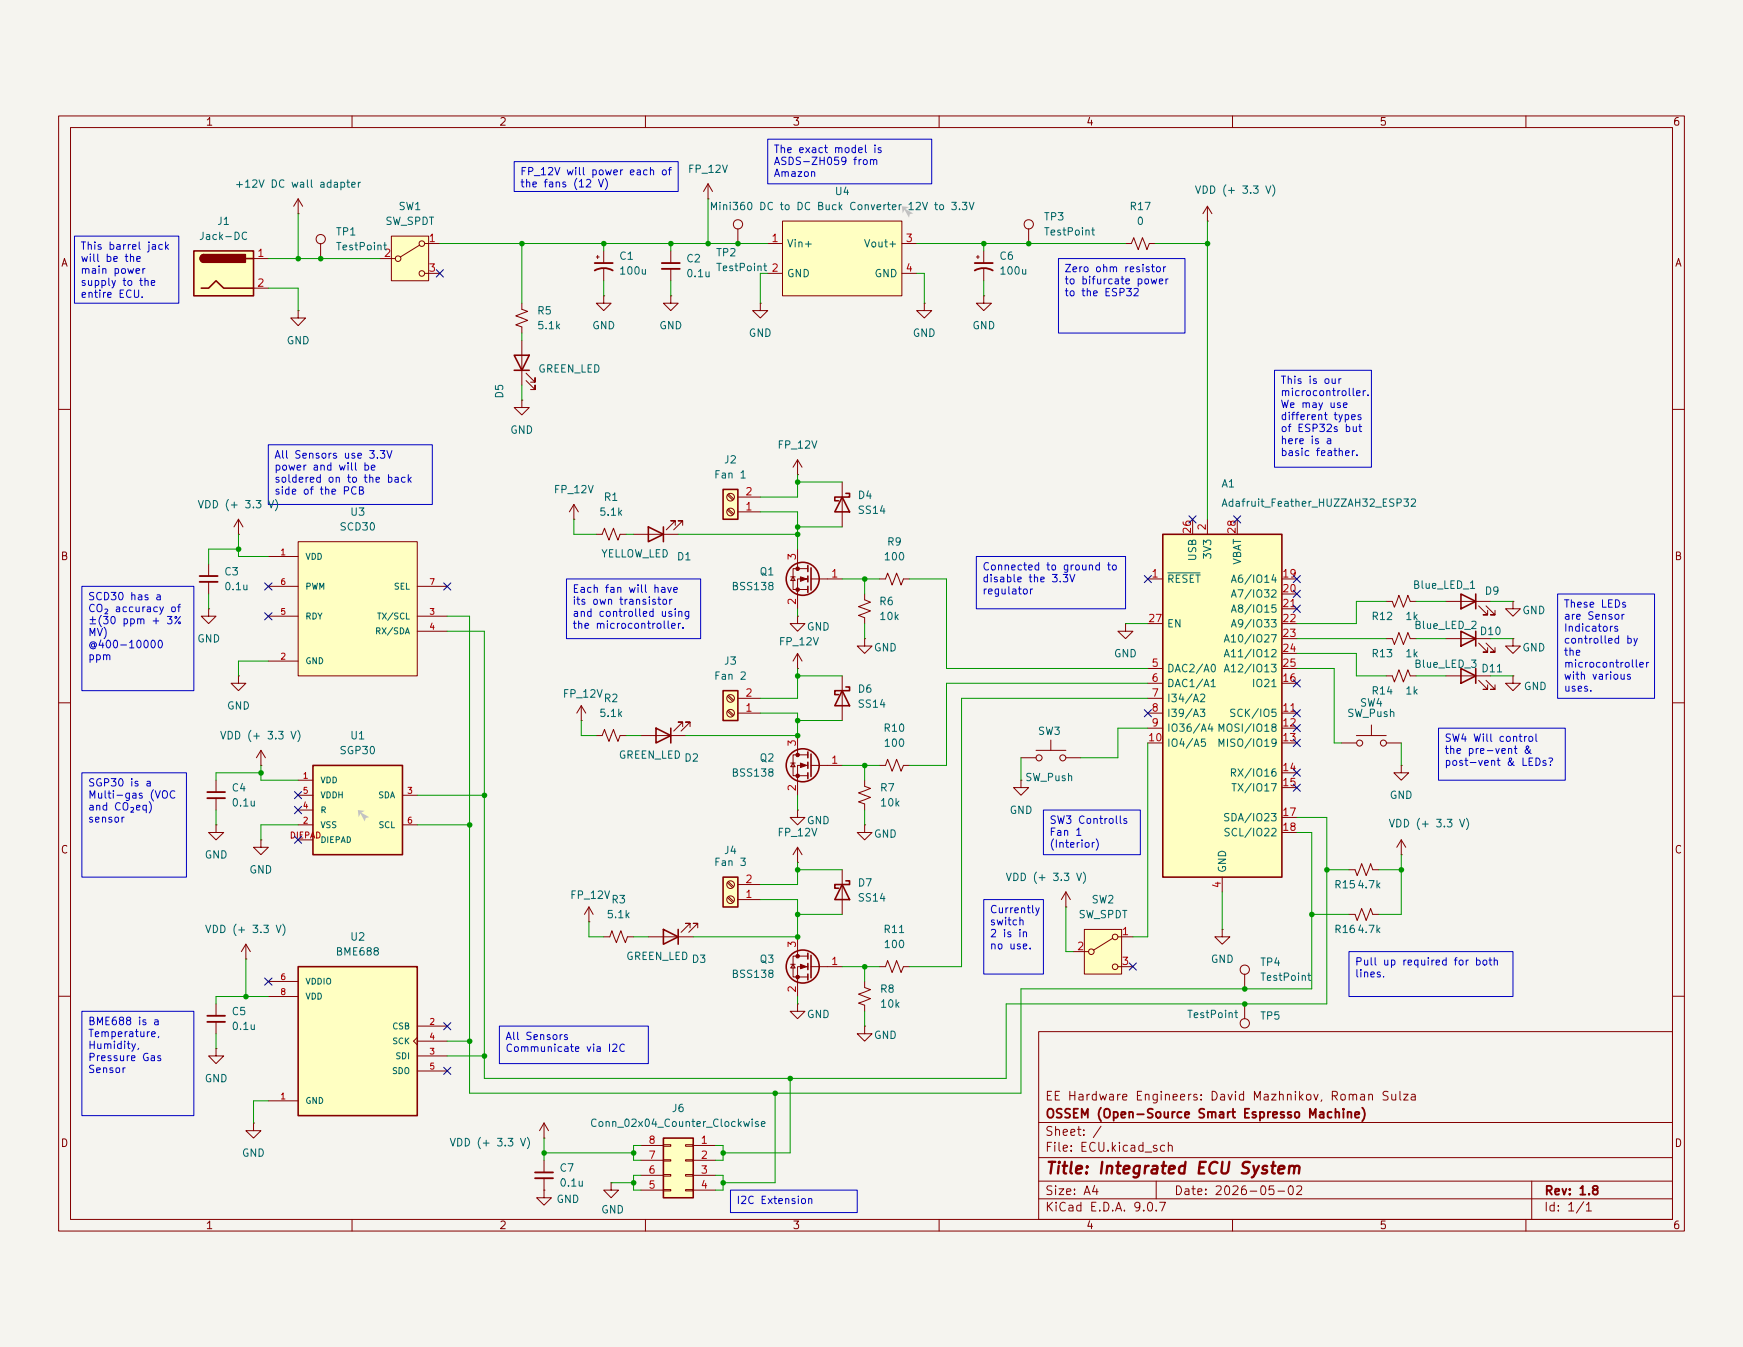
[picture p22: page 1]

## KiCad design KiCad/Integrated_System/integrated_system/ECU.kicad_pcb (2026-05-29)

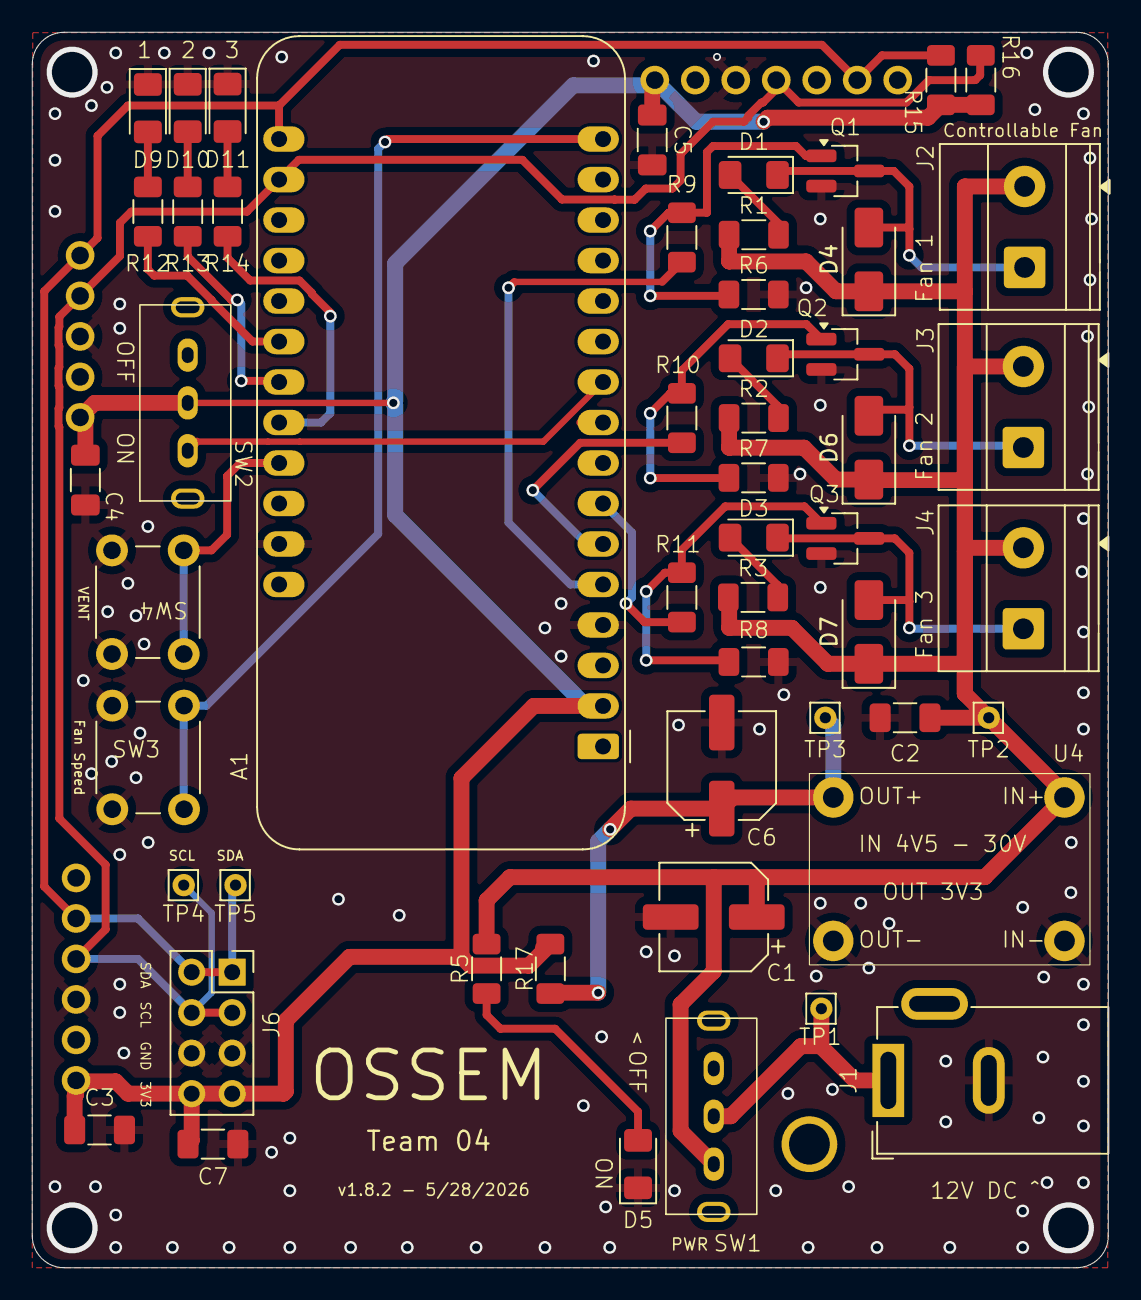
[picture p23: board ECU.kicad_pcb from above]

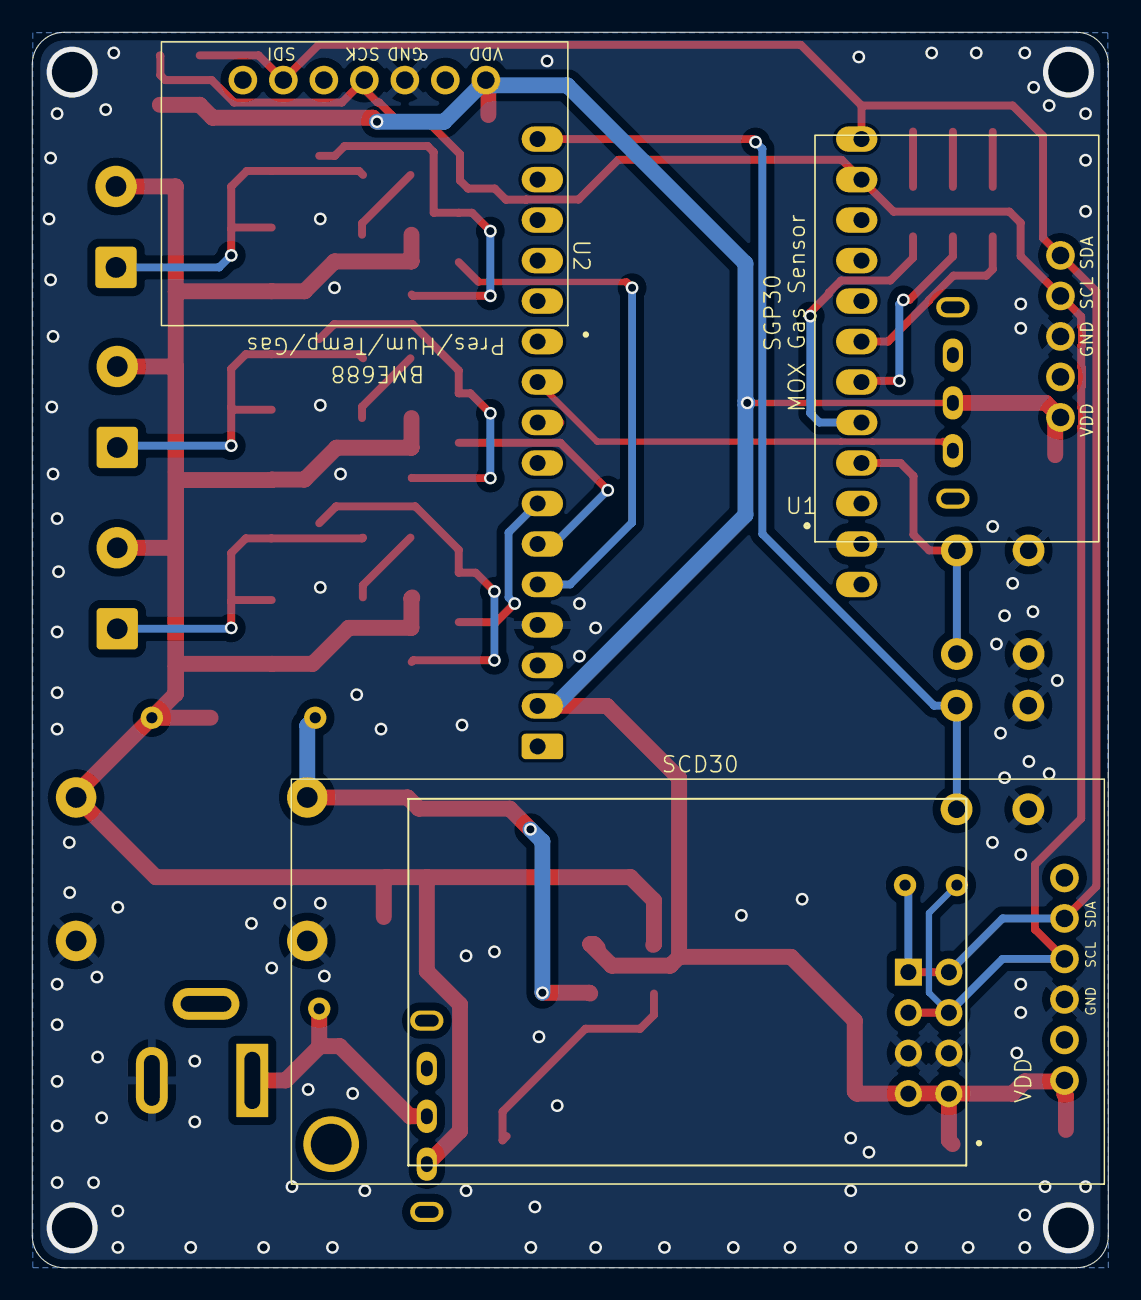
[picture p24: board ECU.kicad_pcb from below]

Board: 2 copper layers, 67.5 x 77.5 mm, 55 parts (3 on the bottom side), 29 nets.

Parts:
A1: Adafruit_Feather_HUZZAH32_ESP32; Adafruit_Feather
C1, C6: 100u; CP_Elec_6.3x7.7
C2, C3, C4, C5, C7: 0.1u; C_1206_3216Metric_Pad1.33x1.80mm_HandSolder
D1, D2, D3, D5: GREEN_LED; LED_1206_3216Metric_Pad1.42x1.75mm_HandSolder
D4, D6, D7: SS14; D_SMA
D9: Blue_LED_1; LED_1206_3216Metric_Pad1.42x1.75mm_HandSolder
D10: Blue_LED_2; LED_1206_3216Metric_Pad1.42x1.75mm_HandSolder
D11: Blue_LED_3; LED_1206_3216Metric_Pad1.42x1.75mm_HandSolder
J1: Jack-DC; BarrelJack_GCT_DCJ200-10-A_Horizontal
J2: Fan 1; TerminalBlock_Phoenix_MKDS-1,5-2-5.08_1x02_P5.08mm_Horizont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
J3: Fan 2; TerminalBlock_Phoenix_MKDS-1,5-2-5.08_1x02_P5.08mm_Horizont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
J4: Fan 3; TerminalBlock_Phoenix_MKDS-1,5-2-5.08_1x02_P5.08mm_Horizont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
J6: Conn_02x04_Counter_Clockwise; PinSocket_2x04_P2.54mm_Vertical
Q1, Q2, Q3: BSS138; SOT-23_Handsoldering
R1, R2, R3, R5: 5.1k; R_1206_3216Metric_Pad1.30x1.75mm_HandSolder
R6, R7, R8: 10k; R_1206_3216Metric_Pad1.30x1.75mm_HandSolder
R9, R10, R11: 100; R_1206_3216Metric_Pad1.30x1.75mm_HandSolder
R12, R13, R14: 1k; R_1206_3216Metric_Pad1.30x1.75mm_HandSolder
R15, R16: 4.7k; R_1206_3216Metric_Pad1.30x1.75mm_HandSolder
R17: 0; R_1206_3216Metric_Pad1.30x1.75mm_HandSolder
SW1, SW2: SW_SPDT; switch_dm
SW3, SW4: SW_Push; SW_PUSH_6mm
TP1, TP2, TP3, TP4, TP5: TestPoint; Pin_D0.7mm_L6.5mm_W1.8mm_FlatFork
U1: SGP30
U2: BME688; PSON80P300X300X100-8N
U3: SCD30; MODULE_SCD30
U4: Mini360 DC to DC Buck Converter 12V to 3.3V; Mini360

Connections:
+12V DC wall adapter: J1.1, SW1.2 (B), TP1.1
FP_12V: C1.1, C2.1, D4.1 (K), D6.1 (K), D7.1 (K), J2.2, J3.2, J4.2, R1.1, R2.1, R3.1, R5.2, SW1.1 (A), TP2.1, U4.1 (Vin+)
GND: A1.4 (GND), A1.27 (EN), C1.2, C2.2, C3.2, C4.2, C5.2, C6.2, C7.2, D5.1 (K), D9.1 (K), D10.1 (K), D11.1 (K), J1.2, J6.5, J6.6, Q1.2 (S), Q2.2 (S), Q3.2 (S), R6.1, R7.1, R8.1, SW3.1, SW4.1, U1.2 (VSS), U2.1 (GND), U3.2 (GND), U4.2 (GND), U4.4 (GND)
unnamed: A1.22 (A9/IO33), R12.2
unnamed: A1.23 (A10/IO27), R13.2
unnamed: A1.24 (A11/IO12), R14.2
unnamed: A1.25 (A12/IO13), SW4.2
unnamed: A1.6 (DAC1/A1), R10.2
unnamed: A1.5 (DAC2/A0), R9.2
unnamed: A1.7 (I34/A2), R11.2
unnamed: A1.10 (IO4/A5), SW2.1 (A)
unnamed: A1.16 (IO21), SW3.2
unnamed: A1.18 (SCL/IO22), J6.3, J6.4, R16.2, TP4.1, U1.6 (SCL), U2.4 (SCK), U3.3 (TX/SCL)
unnamed: A1.17 (SDA/IO23), J6.1, J6.2, R15.2, TP5.1, U1.3 (SDA), U2.3 (SDI), U3.4 (RX/SDA)
unnamed: D1.2 (A), R1.2
unnamed: D1.1 (K), D4.2 (A), J2.1, Q1.3 (D)
unnamed: D2.2 (A), R2.2
unnamed: D2.1 (K), D6.2 (A), J3.1, Q2.3 (D)
unnamed: D3.2 (A), R3.2
unnamed: D3.1 (K), D7.2 (A), J4.1, Q3.3 (D)
unnamed: D5.2 (A), R5.1
unnamed: D9.2 (A), R12.1
unnamed: D10.2 (A), R13.1
unnamed: D11.2 (A), R14.1
unnamed: Q1.1 (G), R6.2, R9.1
unnamed: Q2.1 (G), R7.2, R10.1
unnamed: Q3.1 (G), R8.2, R11.1
unnamed: C6.1, R17.1, TP3.1, U4.3 (Vout+)
VDD (+ 3.3 V): A1.2 (3V3), C3.1, C4.1, C5.1, C7.1, J6.7, J6.8, R15.1, R16.1, R17.2, SW2.2 (B), U1.1 (VDD), U2.8 (VDD), U3.1 (VDD)

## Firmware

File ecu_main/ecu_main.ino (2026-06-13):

// ecu_main.ino
// PSU OSSEM Capstone Team: Hussein Ashkanani, Ethan Budde, David Mazhnikov, Roman Sulza, Clarker Ren
// Faculty Advisors: Dr. Joshua Méndez & Dr. Elliott Gall
//
// brief:
//  initializes ECU environment
//  sets up network connections, I2C connections to sensors, fan connections
//  regularly detects sensor values, updates if novel
//  drives interrupts for buttons to control data marking and fan speed
//  outputs sensor data serially as a stream 
// rev 1.1

// TOP
// libraries
// required libraries
#include "Arduino.h"            // base Arduino library
#include <WiFi.h>               // for WiFi shield or ESP32
#include <Wire.h>               // I2C comms library
#include <Adafruit_Sensor.h>    // arbitrary sensor driver library
#include <ezTime.h>             // WiFi timesync, for timestamps
#include <SPI.h>                // Serial peripheral library

// specific sensor libraries
#include <Adafruit_SCD30.h>     // SCD30 interfacing
#include <Adafruit_SGP30.h>     // SGP30 interfacing
#include <Adafruit_BME680.h>    // BME680 interfacing
//#include <Other_Sensor.h>     // additional sensor libraries go here...

// constants and variables
// sensor LED pin constants
// see ~/KiCad/Integrated_System for value coherence
#define BMEPIN 33
#define SCDPIN 27
#define SGPPIN 12

// barometric pressure constant
#define SEALEVELPRESSURE_HPA (1013.25)

// setup pre-run cycles constant
#define PRERUN_CYCLES 15

// loop delay value
#define LOOP_DELAY 50

// fan, button pin constants
// see ~/KiCad/Integrated_System for value coherence
const int FAN1_PIN = 26;
const int FAN2_PIN = 25;
const int BUTTON1_PIN = 13;
const int BUTTON2_PIN = 21;

// fan-speed PWM constants
const int PWM_FREQ = 25000;
const int PWM_RESOLUTION = 8;

// data highlighting boolean
bool trigger = false;

// fan, button state variables
int fanMode = 0;                // initializes fan to medium speed on startup
int reading[3];                 // +1 indexed 

// fan-speed presets
int fanSpeed[] = {              // 3 modes
  135,                          // medium speed - starting value
  0,                            // off
  255                           // full speed
};

// button debouncing state mechanism variables
int lastButtonReading[3];               // active button  
int stableButtonState[3] = {0, 1, 1};   // active low 0s for both buttons
unsigned long lastDebounceTime = 0;     // time since we last bounced
const unsigned long debounceDelay = 50; // delay (ms) ~= 2x expected bounce time

// sensor Objects
Adafruit_SCD30 scd30;
Adafruit_SGP30 sgp;
Adafruit_BME680 bme(&Wire);

// timezone Object
Timezone myTZ;

// network ssid and password
// credentials of hotspot, router connection, or external device's netword
// Rev2 - needs to be pulled from a file, this current design is "unsafe"
char ssid[]     = "SomeNetwork";        // your SSID goes here...
char password[] = "ThePasscode";        // your SSID's pass goes here...

// counter for fallback timestamping check
int count = 0;
int t_dataBegin = 0;

// fallback timestamping enable/disable
bool dumbTimestamps = false;            // disabled by default

// coherence structs, last/current holders
// BME values struct
struct bmeValues{
  float temp;
  float pres;
  float humid;
  float gasr;
};

// BME current, last state holders
bmeValues bmeCurrent, bmeLast;


struct scdValues{
  float temp;
  float humid;
  float co2;  
};
scdValues scdCurrent, scdLast;

struct sgpValues{
  int tvoc;
  int co2;
};
sgpValues sgpCurrent, sgpLast;

/*
struct newSensorValues{
    int value1;
    float value2;
    long float value3;
};
newSensorValues newCurrent, newLast;
*/

// worker functions
// getPinMode
//   checks pin is valid port, returns pin type
uint32_t getPinMode(uint32_t pin) {
  uint32_t bit = digitalPinToBitMask(pin);      // absolute bitvalue
  uint32_t port = digitalPinToPort(pin);        // port mask

  // if this isn't a pin, we don't care about it
  if (port == NOT_A_PIN) return 0xFF;

  volatile uint32_t *reg = portModeRegister(port);
  volatile uint32_t *out = portOutputRegister(port);

  if (*reg & bit) {
    return OUTPUT;                  // pin is configured as an output
  } else {
    return (*out & bit) ? INPUT_PULLUP : INPUT; // checks if pull-up is active
  }
}

// blinkpin
  //checks pin valid output
  //blinks selected pattern at selected pin
void blinkPin(int pin, int pattern){
  if(getPinMode(pin) != OUTPUT) {
    // todo - add error messaging, logging
    return;
  }
  // blinking patterns for sensor leds
  switch(pattern){
    case 0:                   // blink confirm - 2 long blinks, for setup
      digitalWrite(pin, HIGH);
      delay(500);
      digitalWrite(pin, LOW);
      delay(500);
      digitalWrite(pin, HIGH);
      delay(500);
      digitalWrite(pin, LOW);
      delay(500);
      break;
    case 1:                   // enable LED
      digitalWrite(pin, HIGH);
      break;
    case 2:                   // disable LED
      digitalWrite(pin, LOW);
      delay(20);
      break;
    default:
      return;
  }
}

// setup
void setup() {
  // serial comms
  Serial.begin(115200);
  
  // sensor operation LED enabling
  pinMode(BMEPIN, OUTPUT);
  pinMode(SCDPIN, OUTPUT);
  pinMode(SGPPIN, OUTPUT);

  // pushbutton enabling
  pinMode(BUTTON1_PIN, INPUT_PULLUP);
  pinMode(BUTTON2_PIN, INPUT_PULLUP);

  // fan1, fan2 value setting, enabling
  ledcAttach(FAN1_PIN, PWM_FREQ, PWM_RESOLUTION);
  ledcWrite(FAN1_PIN, fanSpeed[fanMode]);

  ledcAttach(FAN2_PIN, PWM_FREQ, PWM_RESOLUTION);
  ledcWrite(FAN2_PIN, fanSpeed[fanMode]);

  // deprecated - test messaging  
  //Serial.println("ESP32 Feather HUZZAH32 fan control started.");
  //Serial.println("Mode 0: OFF");
  
  // hold sensor pins high for Wi-Fi connection period
  blinkPin(BMEPIN, 1);
  blinkPin(SCDPIN, 1);
  blinkPin(SGPPIN, 1);

  //while (!Serial) delay(10);	// will pause until serial terminal open
	
  // wifi signal chain enable
	WiFi.begin(ssid, password);
	while (WiFi.status() != WL_CONNECTED) {
	  Serial.println("Connecting ...");
    
    // 30s timeout counter    
    if(count == 120){
      Serial.println("cannot connect to wifi, no timestamps");
      break;
    }
    count++;
	delay(250);
  }
	
  // if WiFi connected, print basic network details to serial log
  if(WiFi.status() == WL_CONNECTED){
    count = 0;
    Serial.print("connected to network -> ");
    Serial.println(ssid);  
    waitForSync();
    myTZ.setLocation(F("America/Los_Angeles"));
  }
  
  // disable LEDs, network connection period over
  blinkPin(BMEPIN, 2);
  blinkPin(SCDPIN, 2);
  blinkPin(SGPPIN, 2);

  // sgp wakeup
  if (! sgp.begin()){
    Serial.println("SGP sensor not found :(");
    while (1);
  }
  Serial.print("Found SGP30 serial #");
  Serial.print(sgp.serialnumber[0], HEX);
  Serial.print(sgp.serialnumber[1], HEX);
  Serial.println(sgp.serialnumber[2], HEX);

  //sgp blink confirm
  blinkPin(SGPPIN, 0);

  // scd wakeup
  if (!scd30.begin()) {
    Serial.println("Failed to find SCD30 chip");
    while (1) { delay(10); }
  }
  Serial.println("SCD30 Found!");

  // scd measurement interval
  if (!scd30.setMeasurementInterval(2)) {
    Serial.println("Failed to set measurement interval");
    while(1){ delay(10);}
  }
  Serial.print("Measurement interval: "); Serial.print(scd30.getMeasurementInterval());
  Serial.println(" seconds");

  // scd offset check
  Serial.print("Ambient pressure offset: "); Serial.print(scd30.getAmbientPressureOffset());
  Serial.println(" mBar");
  Serial.print("Altitude offset: ");Serial.print(scd30.getAltitudeOffset());
  Serial.println(" meters");
  Serial.print("Temperature offset: ");Serial.print((float)scd30.getTemperatureOffset()/100.0);
  Serial.println(" degrees C");
  Serial.print("Forced Recalibration reference: ");Serial.print(scd30.getForcedCalibrationReference());
  Serial.println(" ppm");

  // scd self calibration check
  if (!scd30.selfCalibrationEnabled(true)){
    Serial.println("Failed to enable or disable self calibration");
    while(1) { delay(10); }
  } if (scd30.selfCalibrationEnabled()) {
    Serial.print("Self calibration enabled");
  } else {
    Serial.print("Self calibration disabled");
  }
  Serial.println("\n\n");

  // scd blink confirm
  blinkPin(SCDPIN, 0);

  // bme wakeup
  if (!bme.begin()) {
		Serial.println("Could not find a valid BME680 sensor, check wiring!");
		while (1);
	}

  // bme constants init 
	bme.setTemperatureOversampling(BME680_OS_8X);
	bme.setHumidityOversampling(BME680_OS_2X);
	bme.setPressureOversampling(BME680_OS_4X);	
	bme.setIIRFilterSize(BME680_FILTER_SIZE_3);
	bme.setGasHeater(320, 150); // 320*C for 150 ms

  // bme blink confirm
  blinkPin(BMEPIN, 0);

  // change this
  for(int i=0;i<PRERUN_CYCLES;i++){
      scdCurrent.temp = scd30.temperature;
      scdCurrent.humid = scd30.relative_humidity;
      scdCurrent.co2 = scd30.CO2;
  }
}

// loop
void loop() {
  // button check
  // see button routines below
  readButton(BUTTON1_PIN, 1);
  readButton(BUTTON2_PIN, 2);
  
  // timestamp marking to serial stream
  if(trigger == true) {
	  Serial.print("!");
    trigger = false;
  }

  // timestamping
  if(dumbTimestamps == false){          // smart, Wi-Fi timestamps
	  Serial.println(myTZ.dateTime("H:i:s.v"));
	}else if(dumbTimestamps == true){   // dumb, time-since-startup timestamps
    char buffer[10];
    int time = (millis() - t_dataBegin) / 1000; 
    sprintf(buffer, "%03d", ((millis() - t_dataBegin) % 1000));
    Serial.print(time); Serial.print("."); Serial.println(buffer);
  }
 

  // refactor for controlability, testing
  // try/except with a nonblocking timer, scheduling
  scdRead();
  sgpRead();
  bmeRead();

  // small wait, loop
  Serial.println();  
  delay(LOOP_DELAY);
}

// bmeRead
// BME688 value requestor, validator 
void bmeRead(){
  // bme check valid
  if (! bme.performReading()) {
		return;
	} else {
    
    // bme oplight on
    blinkPin(BMEPIN, 1);

    // grab values to current holder
    bmeCurrent.temp = bme.temperature;
    bmeCurrent.pres = bme.pressure / 100.0;
    bmeCurrent.humid = bme.humidity;
    bmeCurrent.gasr = bme.gas_resistance / 1000.0;
  }
  
  // if all values same, sensor has no new values, return
  if((bmeCurrent.temp == bmeLast.temp) && (bmeCurrent.pres == bmeLast.pres) && (bmeCurrent.humid == bmeLast.humid) && (bmeCurrent.gasr == bmeLast.gasr)){
    // bme oplight off
    blinkPin(BMEPIN, 2);
    return;

  // otherwise, we have a new value
  }else{ 
    // bme print block
    Serial.println("[BME BLOCK]");
    Serial.print(bme.temperature); Serial.println("[degC]");
    Serial.print(bme.pressure / 100.0); Serial.println("[hPaPres]");
    Serial.print(bme.humidity); Serial.println("[%humid]");
    Serial.print(bme.gas_resistance / 1000.0); Serial.println("[KOhmsGasR]");
    Serial.println();

    // update state values
    bmeLast = bmeCurrent;
  }
  // bme oplight off
  blinkPin(BMEPIN, 2);
}
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

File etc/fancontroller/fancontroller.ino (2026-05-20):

//Three modes to control fan speed
// Board: Adafruit ESP32 Feather / HUZZAH32


const int FAN_PIN = 26;
const int BUTTON_PIN = 13;

const int PWM_FREQ = 25000;
const int PWM_RESOLUTION = 8;

int fanMode = 0;

int fanSpeed[] = {
  0,
  90,
  160,
  255
};

int lastButtonReading = HIGH;
int stableButtonState = HIGH;
unsigned long lastDebounceTime = 0;
const unsigned long debounceDelay = 50;

void setup() {
  Serial.begin(115200);
  delay(2000);
  pinMode(BUTTON_PIN, INPUT_PULLUP);

  ledcAttach(FAN_PIN, PWM_FREQ, PWM_RESOLUTION);
  ledcWrite(FAN_PIN, fanSpeed[fanMode]);

  Serial.println("ESP32 Feather HUZZAH32 fan control started.");
  Serial.println("Mode 0: OFF");
}

void loop() {
  int reading = digitalRead(BUTTON_PIN);

  if (reading != lastButtonReading) {
    lastDebounceTime = millis();
  }

  if ((millis() - lastDebounceTime) > debounceDelay) {
    if (reading != stableButtonState) {
      stableButtonState = reading;

      if (stableButtonState == LOW) {
        fanMode++;

        if (fanMode > 3) {
          fanMode = 0;
        }

        ledcWrite(FAN_PIN, fanSpeed[fanMode]);

        Serial.print("Fan mode: ");
        Serial.print(fanMode);
        Serial.print(" | PWM: ");
        Serial.println(fanSpeed[fanMode]);
      }
    }
  }

  lastButtonReading = reading;
}

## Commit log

2026-02-28 Fan Control KiCad Files
    [Adjustable_Speed_Controller.kicad_pcb, Adjustable_Speed_Controller.kicad_sch]
2026-02-28 Renamed the title
    [Adjustable_Speed_Controller.kicad_sch]
2026-02-28 Replaced LR7843 footprint
    [Adjustable_Speed_Controller.kicad_sch]
2026-02-28 Rev1.1 with new symbol
    Kicad did a funny thing and decided to update its symbols and pinouts
    [Adjustable_Speed_Controller.kicad_sch]
2026-02-28 Centered the circuit
    [Adjustable_Speed_Controller.kicad_sch]
2026-04-04 New Project
    Made a new project folder for the integrated system for the ECU
    [ECU.kicad_sch, integrated_system.kicad_pcb, integrated_system.kicad_sch]
2026-04-04 Added Components
    Added esp32 and some transistors
    [ECU.kicad_sch]
2026-04-09 Added Sensors
    Made a bunch of changes
    [ECU.kicad_sch]
2026-04-09 Added Notes
    [ECU.kicad_sch]
2026-04-09 changed to bme280
    [ECU.kicad_sch]
2026-04-09 replaced transistors
    [ECU.kicad_sch]
2026-04-13 Replaced with bme680 sensor
    [ECU.kicad_sch]
2026-04-13 Added LEDs
    [ECU.kicad_sch]
2026-04-14 Fixed LED placement
    LED Placement and added switch
    [ECU.kicad_sch]
2026-04-14 Switched to the right pins
    [ECU.kicad_sch]
2026-04-14 Added no connects
    [ECU.kicad_sch]
2026-04-15 rev 1.1
    [ECU.kicad_sch, integrated_system.kicad_sch]
2026-04-16 changed ground
    [ECU.kicad_sch]
2026-04-20 Updated LED schematic
    [ECU.kicad_sch]
2026-04-20 Updated the descriptions
    [ECU.kicad_sch]
2026-04-21 Folder Managment
    [Adjustable_Speed_Controller.kicad_pcb, Adjustable_Speed_Controller.kicad_sch, ECU.kicad_sch, integrated_system.kicad_pcb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]
2026-04-21 Updated Footprint v1.1
    [ECU.kicad_sch]
2026-04-21 Started PCB layout
    [ECU.kicad_pcb, ECU.kicad_sch, integrated_system.kicad_pcb]
2026-04-21 Updated Footprints v1.2
    [ECU.kicad_pcb, ECU.kicad_sch]
2026-04-21 Updated Footpirnt libraries v1.3
    [ECU.kicad_pcb, ECU.kicad_sch]
2026-04-21 PCB Layout started v1.1
    [ECU.kicad_pcb]
2026-04-21 Layout rev 1.2
    [ECU.kicad_pcb]
2026-04-21 quick changes
    [ECU.kicad_pcb]
2026-04-21 changes made
    [ECU.kicad_sch]
2026-04-21 changed wire
    [ECU.kicad_sch]
2026-04-22 Replaced the transistors to BSS138
    BSS138 is SMD type
    [ECU.kicad_pcb, ECU.kicad_sch]
2026-04-22 Changed the net for buck
    [ECU.kicad_pcb]
2026-04-22 Rough Board layout
    [ECU.kicad_pcb]
2026-04-23 made changes
    [ECU.kicad_pcb]
2026-04-23 SGP30 & BME680 Foot print edit
    Made a ton of changes
    [ECU.kicad_pcb]
2026-04-23 Nets Label
    [ECU.kicad_pcb]
2026-04-23 redesign v1.3
    [ECU.kicad_pcb, ECU.kicad_sch]
2026-04-23 Layout Complete
    [ECU.kicad_pcb, ECU.kicad_sch]
2026-04-23 Changed 3d model of esp32
    [ECU.kicad_pcb]
2026-04-23 3d renderings
    [ECU.kicad_pcb]
2026-04-23 v1 Routing
    [ECU.kicad_pcb, ECU.kicad_sch]
2026-04-24 deleted all traces
    [ECU.kicad_pcb]
2026-04-24 deleted pot
    [ECU.kicad_pcb, ECU.kicad_sch]
2026-04-24 added zero ojm resistors and testpoints
    [ECU.kicad_sch]
2026-04-24 added I2C extension
    [ECU.kicad_sch]
2026-04-24 small adjustments
    [ECU.kicad_pcb, ECU.kicad_sch]
2026-04-24 initial routing started
    [ECU.kicad_pcb]
2026-04-24 Routing Complete
    [ECU.kicad_pcb, ECU.kicad_sch]
2026-04-24 added copper ground layers
    [ECU.kicad_pcb]
2026-04-25 added a ton of vias
    [ECU.kicad_pcb, ECU.kicad_sch]
2026-04-25 forgot to route some pins
    [ECU.kicad_pcb]
2026-04-25 Fixed DRC Errors
    One left we need to figure out how to fix it
    [ECU.kicad_pcb]
2026-04-26 Added via
    [ECU.kicad_pcb]
2026-04-27 moved for arduino purposes
2026-04-29 1.6 rev
    [ECU.kicad_pcb, ECU.kicad_sch]
2026-04-29 Routing rev1.6 complete
    [ECU.kicad_pcb]
2026-04-29 ran drc
    [ECU.kicad_pcb]
2026-05-01 Rerouted version 1.7
    [ECU.kicad_pcb, ECU.kicad_sch]
2026-05-01 added ground planes
    [ECU.kicad_pcb]
2026-05-01 added dimensions
    [ECU.kicad_pcb, ECU.kicad_sch]
2026-05-02 fixed a lot of the issues brought up from design review
    [ECU.kicad_pcb, ECU.kicad_sch]
2026-05-02 last checks
    [ECU.kicad_pcb, ECU.kicad_sch]
2026-05-02 uploaded to oshpark
    [ECU.kicad_pcb]
2026-05-03 dimensions added for ME team
    [ECU.kicad_pcb]
2026-05-03 removed dimensions
    [ECU.kicad_pcb]
2026-05-20 changed led
    [ECU.csv]
2026-05-29 updated button2 to pin 21
    [ECU.kicad_sch]
2026-05-29 edited schematic to v1.8.2
    fixed the schematic and layout routing of sw3 gpio 36 to gpio21
    [ECU.kicad_pcb, ECU.kicad_sch]
2026-05-29 changed to ossem
    [ECU.kicad_sch]
